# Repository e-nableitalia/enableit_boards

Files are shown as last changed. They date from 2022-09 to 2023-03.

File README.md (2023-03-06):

# enable-it
e-Nable Italia Bionic Platform

This project aims to create a general purpose hardware platform that can be used to develop bionic/electronics controlled devices

## Boards
### Controllers - controller boards with a general purpose CPU, exposing a standard bus interface (see B2BCB specifications)
* ESP32 Wroom board Rev. B - ESP32 S3 based 

### Debug - debug, testing boards
* Debug Board Rev. A, mating board useful for debug and testing purposes

## Project directory layout
- docs, contains general documents
- schematics,  contains schematics in PDF format
- build, contains CAM Output files for board production
- EAGLE, contains project EAGLE files

## Project updates
220913 - repo init, added project doc & rev. 0.9 of ESP32 controller board

220922 - added debug board, added Rev. B of control board

220927 - updated debug board to Rev. A (added bottom connectors to allow tests of stacked boards)

230305 - added EMG Module - Rev B, changed name to enable-it

## KNOWN ISSUES

- ESP32 Controller board flash programming problem, rework required to fix this issue 
- Power connectors are not correctly aligned in all the boards, rework required to fix this issue
- Wrong height of 40pin connectors (4mm instead of 3mm)
- EMG Module power issue: short circuitt between AVDD & AVSS (PS$32 AVSS connected to V+ instead of V-)

## LIMITATION OF LIABILITY.
UNDER NO CIRCUMSTANCES AND UNDER NO LEGAL THEORY, WHETHER TORT (INCLUDING NEGLIGENCE), CONTRACT, OR OTHERWISE, SHALL YOU, THE INITIAL DEVELOPER, ANY OTHER CONTRIBUTOR, OR ANY DISTRIBUTOR OF COVERED CODE, OR ANY SUPPLIER OF ANY OF SUCH PARTIES, BE LIABLE TO ANY PERSON FOR ANY INDIRECT, SPECIAL, INCIDENTAL, OR CONSEQUENTIAL DAMAGES OF ANY CHARACTER INCLUDING, WITHOUT LIMITATION, DAMAGES FOR LOSS OF GOODWILL, WORK STOPPAGE, COMPUTER FAILURE OR MALFUNCTION, OR ANY AND ALL OTHER COMMERCIAL DAMAGES OR LOSSES, EVEN IF SUCH PARTY SHALL HAVE BEEN INFORMED OF THE POSSIBILITY OF SUCH DAMAGES. THIS LIMITATION OF LIABILITY SHALL NOT APPLY TO LIABILITY FOR DEATH OR PERSONAL INJURY RESULTING FROM SUCH PARTY'S NEGLIGENCE TO THE EXTENT APPLICABLE LAW PROHIBITS SUCH LIMITATION. SOME JURISDICTIONS DO NOT ALLOW THE EXCLUSION OR LIMITATION OF INCIDENTAL OR CONSEQUENTIAL DAMAGES, SO THIS EXCLUSION AND LIMITATION MAY NOT APPLY TO YOU.

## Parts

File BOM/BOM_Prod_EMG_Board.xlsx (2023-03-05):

 |  |  | BOM
Item # | *Designator | *Qty | Manufacturer | *Mfg Part # | Description / Value | *Package/Footprint | Type | Your Instructions / Notes
1 | C10, C22, C24, C62, C63, C66 | 6 | Murata | GRM155R71H104KE14D | Multilayer Ceramic Capacitors MLCC - SMD/SMT .1UF 50V 10% 0402 | C0402 | SMD
2 | R4, R7, R55, R56 | 4 | Panasonic | ERJ-2RKF1002X | Thick Film Resistors - SMD 0402 10Kohms 1% AEC-Q200 | R0402 | SMD
3 | R1, R5, R9, R12, R15, R18, R21, R24, R27, R30, R33, R36, R39, R42, R51, R54 | 16 | Panasonic | ERJ-2GEJ106X | Thick Film Resistors - SMD 0402 10Mohms 5% Tol AEC-Q200 | R0402 | SMD
4 | C23 | 1 | Murata | GRM155R60J106ME15D | Multilayer Ceramic Capacitors MLCC - SMD/SMT 10UF 6.3V 20% 0402 | C0402 | SMD
5 | R3, R8, R11, R14, R17, R20, R23, R26, R29, R32, R35, R38, R41, R44, R53, R59 | 16 | Panasonic | ERJ-PA2F1001X | Thick Film Resistors - SMD 0402 1% 1.0Kohm Anti-Surge AEC-Q200 | R0402 | SMD
6 | R2, R6, R10, R13, R16, R19, R22, R25, R28, R31, R34, R37, R40, R43, R52, R58 | 16 | Panasonic | ERJ-PA2F1004X | Thick Film Resistors - SMD 0402 1% 1.0Mohm Anti-Surge AEC-Q200 | R0402 | SMD
7 | C64 | 1 | Murata | GRT1555C1H102JA02D | Multilayer Ceramic Capacitors MLCC - SMD/SMT 1000PF 50V 5% 0402 | C0402 | SMD
8 | C1, C5, C7, C11, C13, C15, C25, C27, C29, C31, C33, C35, C37, C39, C53, C55 | 16 | Murata | GRM155R61E105MA12D | Multilayer Ceramic Capacitors MLCC - SMD/SMT 1.0UF 25V 20% 0402 | C0402 | SMD
9 | C3, C4, C9, C17, C18, C19, C20, C21, C57, C59, C60, C61, C65 | 13 | Murata | GRM155R61E105MA12D | Multilayer Ceramic Capacitors MLCC - SMD/SMT 1.0UF 25V 20% 0402 | C0402 | SMD
10 | J9, J10 | 2 | ERNI | 224920 | Board to Board & Mezzanine Connectors 9P 0.8MM VERT FML CLASS 4 3MM SMT | 224920 | SMD
11 | C58 | 1 | Murata | GRM158R61A226ME15D | Multilayer Ceramic Capacitors MLCC - SMD/SMT 0402(1005M)/X5R/22uF/ +/-20%/10 VDC | C0402 | SMD
12 | C2, C6, C8, C12, C14, C16, C26, C28, C30, C32, C34, C36, C38, C40, C54, C56 | 16 | Murata | GRM1555C1H471FA01D | Multilayer Ceramic Capacitors MLCC - SMD/SMT 470PF 50V 1% 0402 | C0402 | SMD
13 | J1, J2 | 2 | Hirose | BM23FR0.6-8DS-0.35V(895) | Board to Board & Mezzanine Connectors 8P RCPT STRGHT SMT SIGNAL ONLY | BM23FR068DS035V895 | SMD
14 | J5 | 1 | Hirose | DF12NB-40DS-0.5V(51) | Board to Board & Mezzanine Connectors CONN RCPT 40POS SMD | DF12NB40DS05V51 | SMD
15 | J7 | 1 | Hirose | DF12NB(4.0)-40DP-0.5V(51) | Board to Board & Mezzanine Connectors CONN HDR 40POS SMD G | DF12NB4040DP05V51 | SMD
16 | S1 | 1 | TE Connectivity / Alcoswitch | GDH04S04 | DIP Switches/SIP Switches SPST 4POS REC RCKR SMT DIP SWITCH | SOIC127P813X256-8N | SMD
17 | PS1 | 1 | Maxim Integrated | MAX1697UEUT+T | MAXIM INTEGRATED PRODUCTS - MAX1697UEUT+T - CHARGE PUMP, INVERTING, SOT-23-6 | SOT95P280X145-6N | SMD
18 | U21 | 1 | Texas Instruments | TPS73225MDBVREP | LDO Voltage Regulators Mil Enh Cap-Free NMOS 250-mA LDO Reg | SOT23-5 | SMD
19 | U1 | 1 | Texas Instruments | ADS1298IPAG | Analog to Digital Converters - ADC 8Ch,24B ADC | TQFP-64 | SMD
20 | U10 | 1 | Texas Instruments | ESD401DPYR | ESD Suppressors / TVS Diodes 0.77-pF, +/-5.5V, +/-24-kV ESD protection diode in 0402 package 2-X1SON -40 to 125 | DPY0002A | SMD
21 | U12 | 1 | Texas Instruments | ESD401DPYR | ESD Suppressors / TVS Diodes 0.77-pF, +/-5.5V, +/-24-kV ESD protection diode in 0402 package 2-X1SON -40 to 125 | DPY0002A | SMD
22 | U13 | 1 | Texas Instruments | ESD401DPYR | ESD Suppressors / TVS Diodes 0.77-pF, +/-5.5V, +/-24-kV ESD protection diode in 0402 package 2-X1SON -40 to 125 | DPY0002A | SMD
23 | U14 | 1 | Texas Instruments | ESD401DPYR | ESD Suppressors / TVS Diodes 0.77-pF, +/-5.5V, +/-24-kV ESD protection diode in 0402 package 2-X1SON -40 to 125 | DPY0002A | SMD
24 | U15 | 1 | Texas Instruments | ESD401DPYR | ESD Suppressors / TVS Diodes 0.77-pF, +/-5.5V, +/-24-kV ESD protection diode in 0402 package 2-X1SON -40 to 125 | DPY0002A | SMD
25 | U17 | 1 | Texas Instruments | ESD401DPYR | ESD Suppressors / TVS Diodes 0.77-pF, +/-5.5V, +/-24-kV ESD protection diode in 0402 package 2-X1SON -40 to 125 | DPY0002A | SMD
26 | U11, U18 | 2 | Texas Instruments | ESD401DPYR | ESD Suppressors / TVS Diodes 0.77-pF, +/-5.5V, +/-24-kV ESD protection diode in 0402 package 2-X1SON -40 to 125 | DPY0002A | SMD
27 | U2 | 1 | Texas Instruments | ESD401DPYR | ESD Suppressors / TVS Diodes 0.77-pF, +/-5.5V, +/-24-kV ESD protection diode in 0402 package 2-X1SON -40 to 125 | DPY0002A | SMD
28 | U3 | 1 | Texas Instruments | ESD401DPYR | ESD Suppressors / TVS Diodes 0.77-pF, +/-5.5V, +/-24-kV ESD protection diode in 0402 package 2-X1SON -40 to 125 | DPY0002A | SMD
29 | U4 | 1 | Texas Instruments | ESD401DPYR | ESD Suppressors / TVS Diodes 0.77-pF, +/-5.5V, +/-24-kV ESD protection diode in 0402 package 2-X1SON -40 to 125 | DPY0002A | SMD
30 | U5 | 1 | Texas Instruments | ESD401DPYR | ESD Suppressors / TVS Diodes 0.77-pF, +/-5.5V, +/-24-kV ESD protection diode in 0402 package 2-X1SON -40 to 125 | DPY0002A | SMD
31 | U6 | 1 | Texas Instruments | ESD401DPYR | ESD Suppressors / TVS Diodes 0.77-pF, +/-5.5V, +/-24-kV ESD protection diode in 0402 package 2-X1SON -40 to 125 | DPY0002A | SMD
32 | U7 | 1 | Texas Instruments | ESD401DPYR | ESD Suppressors / TVS Diodes 0.77-pF, +/-5.5V, +/-24-kV ESD protection diode in 0402 package 2-X1SON -40 to 125 | DPY0002A | SMD
33 | U8 | 1 | Texas Instruments | ESD401DPYR | ESD Suppressors / TVS Diodes 0.77-pF, +/-5.5V, +/-24-kV ESD protection diode in 0402 package 2-X1SON -40 to 125 | DPY0002A | SMD
34 | U9 | 1 | Texas Instruments | ESD401DPYR | ESD Suppressors / TVS Diodes 0.77-pF, +/-5.5V, +/-24-kV ESD protection diode in 0402 package 2-X1SON -40 to 125 | DPY0002A | SMD
Need a quick and accurante quote? Need an efficient production? Please read SMT Ordering Necessary Files & Info in 1 minute. Thank you very much! (https://www.pcbway.com/smt_ordering_guide.html)
Click for Instructions on How to Create a BOM (https://www.pcbway.com/blog/PCB_Assembly/How_to_Build_a_BOM__Bill_Of_Materials_.html)

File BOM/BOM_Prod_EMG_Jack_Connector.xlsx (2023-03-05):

 |  |  | BOM
Item # | *Designator | *Qty | Manufacturer | *Mfg Part # | Description / Value | *Package/Footprint | Type | Your Instructions / Notes
1 | J1, J6 | 2 | Hirose | BM23FR0.6-8DP-0.35V(51) | Board to Board & Mezzanine Connectors 8P HDR STRGHT SMT SIGNAL ONLY | BM23FR068DP035V51 | SMD
2 | J2, J3, J4, J7, J8, J9, J10, J17 | 6 | CUI | SJ1-3533N | 3.5 mm Right-Angle Stereo Jack, 3 Pin PCB Mount, Threaded w/ Nut Check | CUI_SJ1-3533 | thru-hole
Need a quick and accurante quote? Need an efficient production? Please read SMT Ordering Necessary Files & Info in 1 minute. Thank you very much! (https://www.pcbway.com/smt_ordering_guide.html)
Click for Instructions on How to Create a BOM (https://www.pcbway.com/blog/PCB_Assembly/How_to_Build_a_BOM__Bill_Of_Materials_.html)

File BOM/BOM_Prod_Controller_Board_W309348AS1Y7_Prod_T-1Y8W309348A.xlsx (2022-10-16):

 |  |  | W309348AS1Y7 T-1Y8W309348A 05PCS BOM (Bill of Materials)
Item # | *Designator | *Qty | Manufacturer | *Mfg Part # | Description / Value | *Package/Footprint | Type | Your Instructions / Notes
1 | J2 | 1 |  |  | SMD solder JUMPER , | SJ | DNS
2 | J8 | 1 | Hirose | ZX62-AB-5PA | USB Connectors MICRO AB RECEPT RA SMT BTTM MNT | ZX62-AB-5PA | SMD
3 | C3 | 1 | Murata | GRM155R71H104KE14D | Multilayer Ceramic Capacitors MLCC - SMD/SMT .1UF 50V 10% 0402 | C0402 | SMD
4 | R9, R10 | 2 | Panasonic | ERJ-2GE0R00X | Thick Film Resistors - SMD 0402 Zero ohms 5% Tol AEC-Q200 | R0402 | SMD
5 | R3 | 1 | Panasonic | ERJ-2RKF1003X | Thick Film Resistors - SMD 0402 100Kohms 1% AEC-Q200 | R0402 | SMD
6 | R1 | 1 | Panasonic | ERJ-2RKF1002X | Thick Film Resistors - SMD 0402 10Kohms 1% AEC-Q200 | R0402 | SMD
7 | C6 | 1 | Murata | GRM155R60J106ME15D | Multilayer Ceramic Capacitors MLCC - SMD/SMT 10UF 6.3V 20% 0402 | C0402 | SMD
8 | R6 | 1 | Panasonic | ERJ-PA2F1004X | Thick Film Resistors - SMD 0402 1% 1.0Mohm Anti-Surge AEC-Q200 | R0402 | SMD
9 | R11 | 1 | Panasonic | ERJ-PA2F1001X | Thick Film Resistors - SMD 0402 1% 1.0Kohm Anti-Surge AEC-Q200 | R0402 | SMD
10 | C5 | 1 | Murata | GRM155R61E105MA12D | Multilayer Ceramic Capacitors MLCC - SMD/SMT 1.0UF 25V 20% 0402 | C0402 | SMD
11 | R2 | 1 | Panasonic | ERJ-2RKF2212X | Thick Film Resistors - SMD 0402 22.1Kohms 1% AEC-Q200 | R0402 | SMD
12 | J3 | 1 | ERNI | 224920 | Board to Board & Mezzanine Connectors 9P 0.8MM VERT FML CLASS 4 3MM SMT | 224920 | SMD
13 | C2 | 1 | Murata | GRM158R61A226ME15D | Multilayer Ceramic Capacitors MLCC - SMD/SMT 0402(1005M)/X5R/22uF/ +/-20%/10 VDC | C0402 | SMD
14 | C1, C4 | 2 | Samsung | CL10A226MO7JZNC | Multilayer Ceramic Capacitors MLCC - SMD/SMT 22uF+/-20% 16V X5R 1 0603 | C0603 | SMD
15 | R7 | 1 | Panasonic | ERJ-2RHD243X | Thick Film Resistors - SMD 0402 24Kohms 0.5%AEC-Q200 | R0402 | SMD
16 | R5 | 1 | Panasonic | ERJ-2RKF3902X | Thick Film Resistors - SMD 0402 39Kohms 1% AEC-Q200 | R0402 | SMD
17 | C11 | 1 | Kemet | C0805C472KDRACTU | Multilayer Ceramic Capacitors MLCC - SMD/SMT 1kV 4700pF X7R 0805 10% | 0805-R2013X50N | SMD
18 | PWR | 1 | MOLEX | 530470310 | Headers & Wire Housings VERTICAL HDR 3P | 53047-03 | SMD
19 | I2C | 1 | MOLEX | 532610271 | Headers & Wire Housings 1.25MM HDR 2 CKT Right-Angle | 53261-02 | SMD
20 | R4, R8 | 2 | Panasonic | ERJ-2RKF7502X | Thick Film Resistors - SMD 0402 75Kohms 1% AEC-Q200 | R0402 | SMD
21 | IC3 | 1 | Silicon Labs | CP2102N-A02-GQFN20R | USB Interface IC USBXpress - USB to UART Bridge QFN20 | CP2102NA02GQFN20 | SMD
22 | J1 | 1 | Hirose | DF12NB(4.0)-40DP-0.5V(51) | Board to Board & Mezzanine Connectors CONN HDR 40POS SMD G | DF12NB4040DP05V51 | SMD
23 | IC1 | 1 | Espressif Systems | ESP32-S3-WROOM-1-N8R2 | Multiprotocol Modules SMD Module, ESP32-S3R2, 2 MB PSRAM, 8 MB SPI Flash, PCB Antenna | ESP32S3WROOM1N8R2 | SMD
24 | S1 | 1 | C & K COMPONENTS | KMT211NGLFS | Tactile Switches SPST N.O. GULLWING FOR SMT | KMT211NGLFS | SMD
25 | IC2 | 1 | Monolithic Power Systems (MPS) | MPM3610GQV-P | Switching Voltage Regulators 24V/1A DC/DC Mini- Module Reg w Inductr | MPM3610GQVP | SMD
26 | D2 | 1 | Nexperia | PMEG6020AELPX | Schottky Diodes & Rectifiers PMEG6020AELP/SOD128/FlatPower | SODFL4725X110N | SMD
27 | D1 | 1 | Nexperia | PRTR5V0U2X,215 | ESD Suppressors / TVS Diodes PRTR5V0U2X/SOT143/SOT4 | SOT190P230X110-4N | SMD
Need a quick and accurante quote? Need an efficient production? Please read SMT Ordering Necessary Files & Info in 1 minute. Thank you very much! (https://www.pcbway.com/smt_ordering_guide.html)
Click for Instructions on How to Create a BOM (https://www.pcbway.com/blog/PCB_Assembly/How_to_Build_a_BOM__Bill_Of_Materials_.html)

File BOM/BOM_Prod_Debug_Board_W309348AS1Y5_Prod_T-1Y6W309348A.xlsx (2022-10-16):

 |  |  | W309348AS1Y7 T-1Y8W309348A 05PCS BOM (Bill of Materials)
Item # | *Designator | *Qty | Manufacturer | *Mfg Part # | Description / Value | *Package/Footprint | Type | Your Instructions / Notes
1 | J3, J6 | 2 | ERNI | 224920 | Board to Board & Mezzanine Connectors 9P 0.8MM VERT FML CLASS 4 3MM SMT | 224920 | SMD
2 | J5 | 1 | Hirose | DF12NB-40DS-0.5V(51) | Board to Board & Mezzanine Connectors CONN RCPT 40POS SMD | DF12NB40DS05V51 | SMD
3 | J7 | 1 | Hirose | DF12NB(4.0)-40DP-0.5V(51) | Board to Board & Mezzanine Connectors CONN HDR 40POS SMD G | DF12NB4040DP05V51 | SMD
4 | J4 | 1 | Harwin | M50-3031042 | Headers & Wire Housings 10 WAY SIL VERT PC TAIL SKT | M503031042 | DNS | Do not populate
5 | J1, J2 | 2 | Harwin | M50-3032042 | Headers & Wire Housings 20 WAY SIL VERT PC TAIL SKT | M503032042 | DNS | Do not populate
6
7
8
9
10
11
12
13
14
15
16
17
18
19
20
21
22
23
24
25
26
27
Need a quick and accurante quote? Need an efficient production? Please read SMT Ordering Necessary Files & Info in 1 minute. Thank you very much! (https://www.pcbway.com/smt_ordering_guide.html)
Click for Instructions on How to Create a BOM (https://www.pcbway.com/blog/PCB_Assembly/How_to_Build_a_BOM__Bill_Of_Materials_.html)

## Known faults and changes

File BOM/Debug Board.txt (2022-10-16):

Partlist exported from H:/Drive condivisi/e-Nable Italia/R&D Projects/EAGLE/e-Bionic/Debug Board.sch at 28/09/2022 07:59

Qty Value                     Device                    Package           Parts  Description                                                             DESCRIPTION                                                             HEIGHT MANUFACTURER_NAME MANUFACTURER_PART_NUMBER  MOUSER_PART_NUMBER   MOUSER_PRICE-STOCK                                                                                           
2   224920                    224920                    224920            J3, J6 Board to Board & Mezzanine Connectors 9P 0.8MM VERT FML CLASS 4 3MM SMT Board to Board & Mezzanine Connectors 9P 0.8MM VERT FML CLASS 4 3MM SMT 3.96mm ERNI              224920                    305-224920           https://www.mouser.co.uk/ProductDetail/ERNI/224920?qs=Kh9WxvXxjWmfiTh6L%2FvUxg%3D%3D                         
1   DF12NB-40DS-0.5V_51_      DF12NB-40DS-0.5V_51_      DF12NB40DS05V51   J5     Board to Board & Mezzanine Connectors CONN RCPT 36POS SMD               Board to Board & Mezzanine Connectors CONN RCPT 36POS SMD               2.9mm  Hirose            DF12NB-40DS-0.5V(51)      798-DF12NB40DS0551   https://www.mouser.co.uk/ProductDetail/Hirose-Connector/DF12NB-40DS-0.5V51?qs=DPoM0jnrROV9WbEBnogTmg%3D%3D   
1   DF12NB_4.0_-40DP-0.5V_51_ DF12NB_4.0_-40DP-0.5V_51_ DF12NB4040DP05V51 J7     Board to!! Board !! & Mezzanine Connectors CONN HDR 40POS SMD G         Board to!! Board !! & Mezzanine Connectors CONN HDR 40POS SMD G         3.5mm  Hirose            DF12NB(4.0)-40DP-0.5V(51) 798-DF12NB4040DP0551 https://www.mouser.co.uk/ProductDetail/Hirose-Connector/DF12NB4.0-40DP-0.5V51?qs=DPoM0jnrROUKZpllIjGjYw%3D%3D
1   M50-3031042               M50-3031042               M503031042        J4     Headers & Wire Housings 10 WAY SIL VERT PC TAIL SKT                     Headers & Wire Housings 10 WAY SIL VERT PC TAIL SKT                     4.55mm Harwin            M50-3031042               855-M50-3031042      https://www.mouser.co.uk/ProductDetail/Harwin/M50-3031042?qs=%252BdQmOuGyFcGr7bDrWORUuA%3D%3D                
2   M50-3032042               M50-3032042               M503032042        J1, J2 Headers & Wire Housings 20 WAY SIL VERT PC TAIL SKT                     Headers & Wire Housings 20 WAY SIL VERT PC TAIL SKT                     4.55mm Harwin            M50-3032042               855-M50-3032042      https://www.mouser.co.uk/ProductDetail/Harwin/M50-3032042?qs=%252BdQmOuGyFcG1Q4VMzC2p1Q%3D%3D

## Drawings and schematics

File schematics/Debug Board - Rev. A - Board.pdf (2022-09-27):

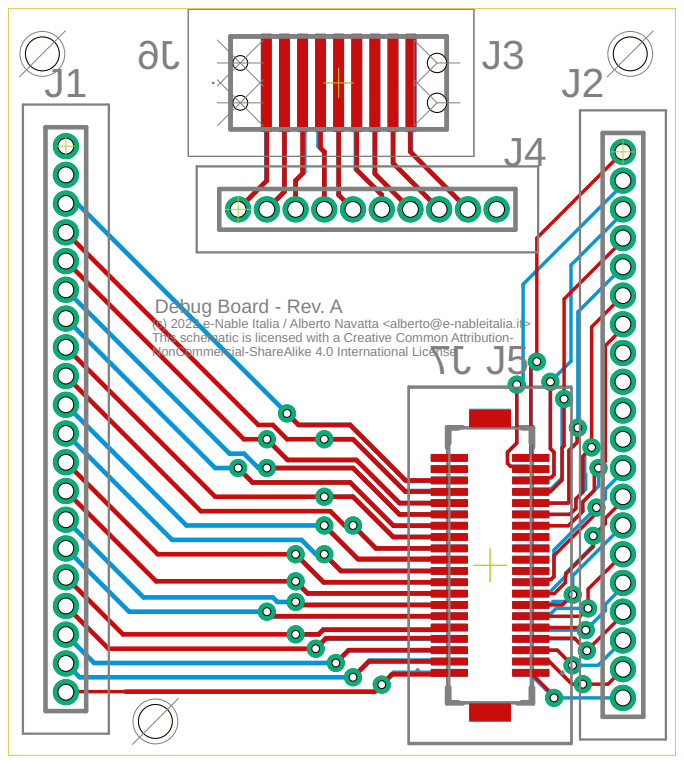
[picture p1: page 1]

Debug Board - Rev. A
(c) 2022 e-Nable Italia / Alberto Navatta <alberto@e-nableitalia.it>
This schematic is licensed with a Creative Common Attribution- NonCommercial-ShareAlike 4.0 International License

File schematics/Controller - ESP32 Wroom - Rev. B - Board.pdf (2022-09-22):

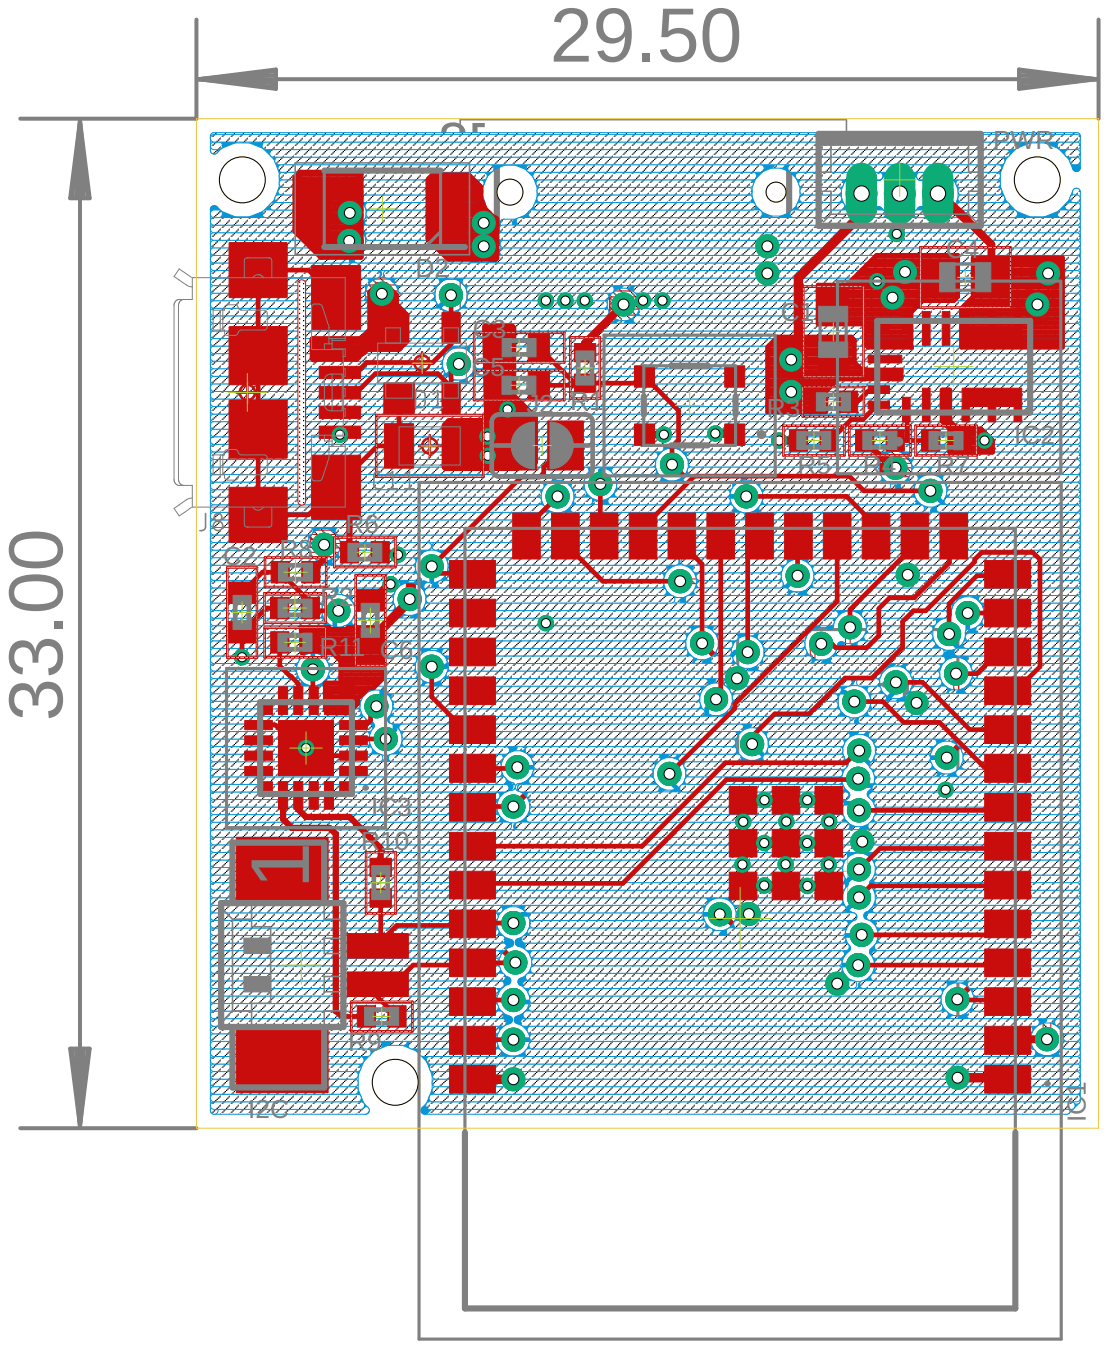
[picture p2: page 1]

(c) 2022 e-Nable Italia / Alberto Navatta <alberto@e-nableitalia.it> This schematic is licensed with a Creative Common Attribution- NonCommercial-ShareAlike 4.0 International License Controller Board - ESP32 Wroom - Rev. A1J 3J 1 33.00 29.50 C5 IC1 J2 R1 C3 D2 IC2 R3 C4 R5 R4 R7 R6 C1 I2C IC3 R2 C R8 2 R9R10 R11 C6 PWR

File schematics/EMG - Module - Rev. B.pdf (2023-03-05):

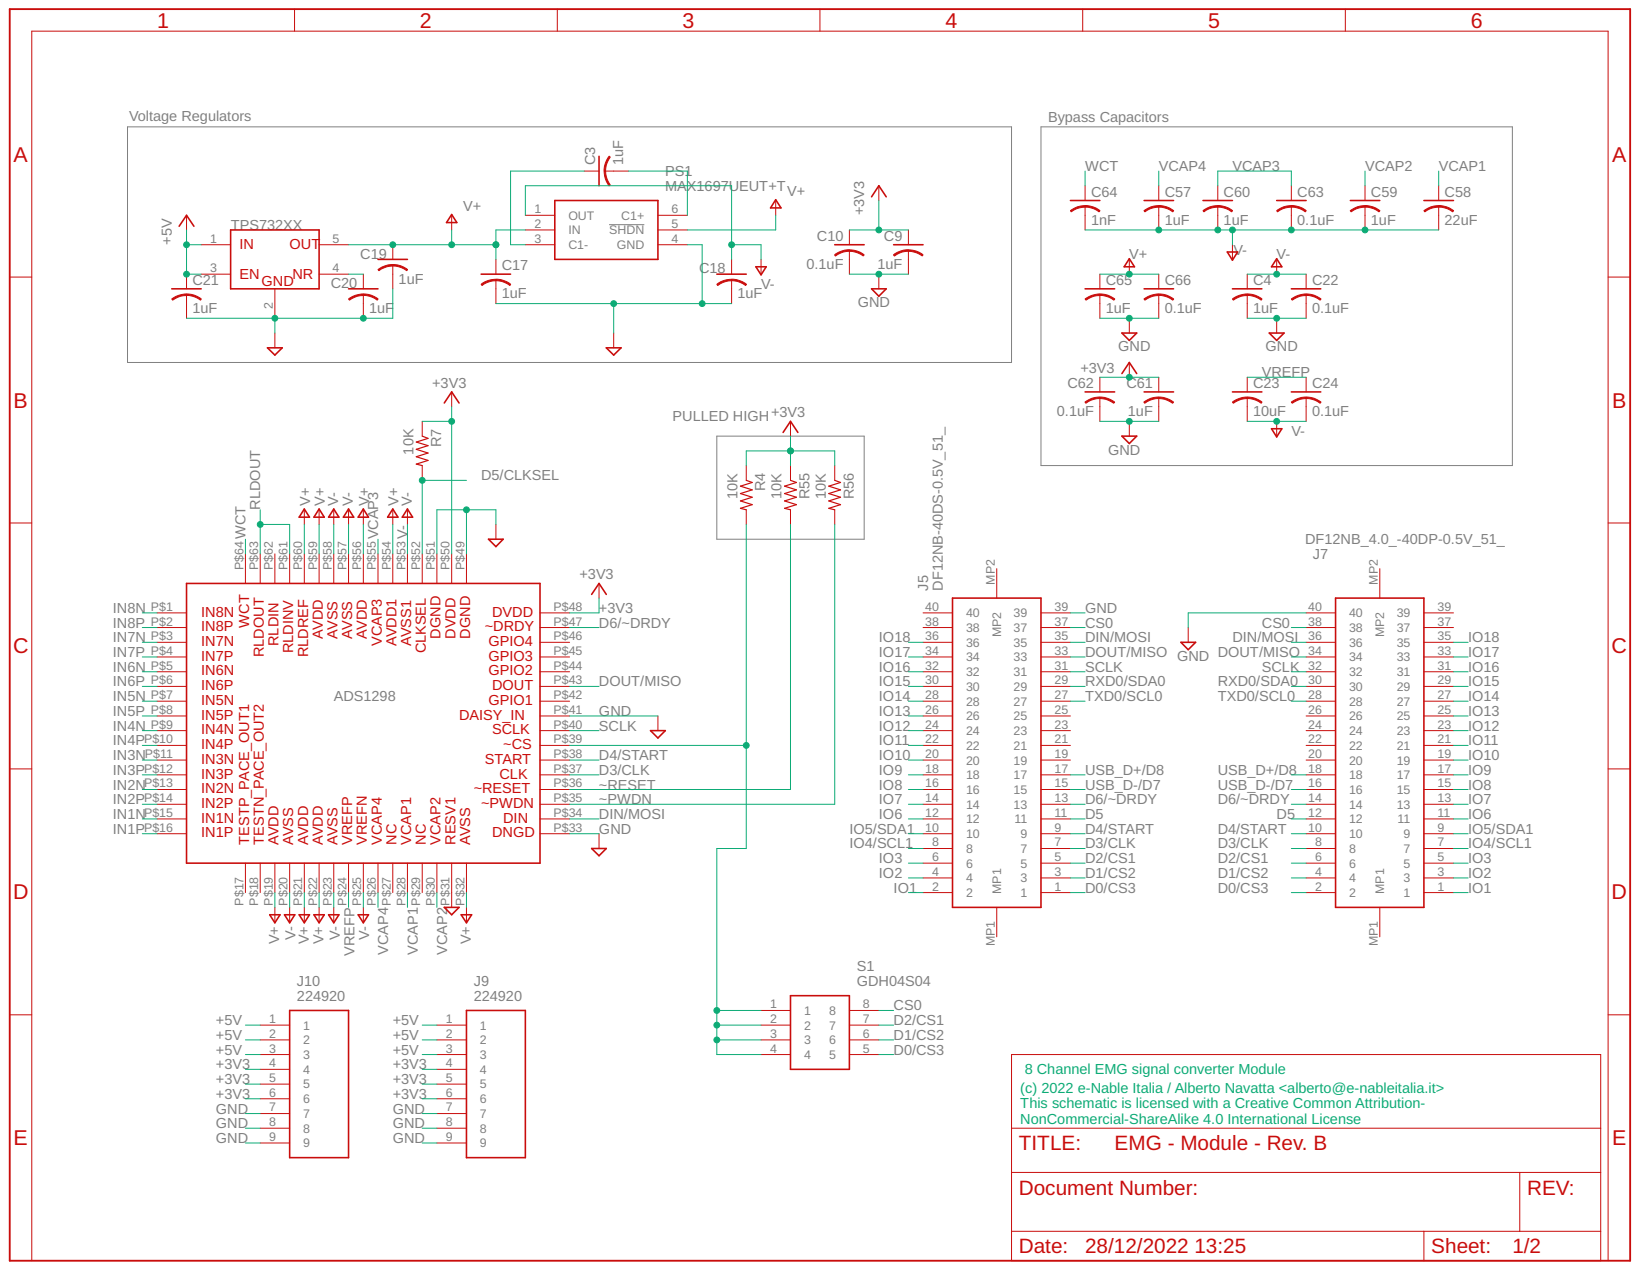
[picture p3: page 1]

8 Channel EMG signal converter Module
(c) 2022 e-Nable Italia / Alberto Navatta <alberto@e-nableitalia.it> This schematic is licensed with a Creative Common Attribution- NonCommercial-ShareAlike 4.0 International License

Document Number: | REV:

Date: 28/12/2022 13:25 | Sheet: 1/2

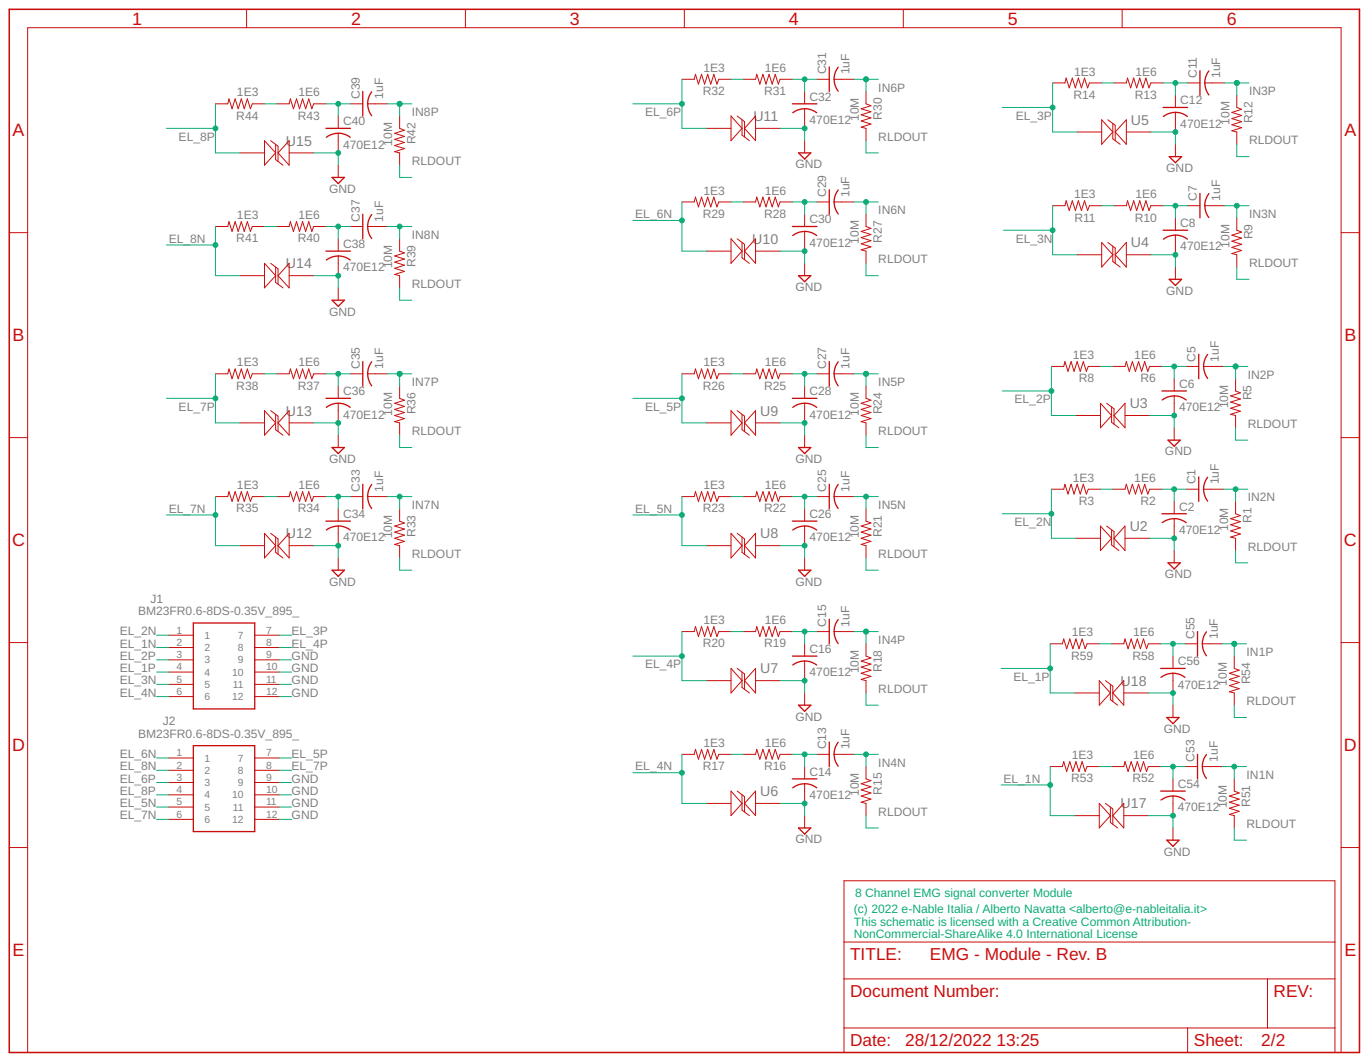
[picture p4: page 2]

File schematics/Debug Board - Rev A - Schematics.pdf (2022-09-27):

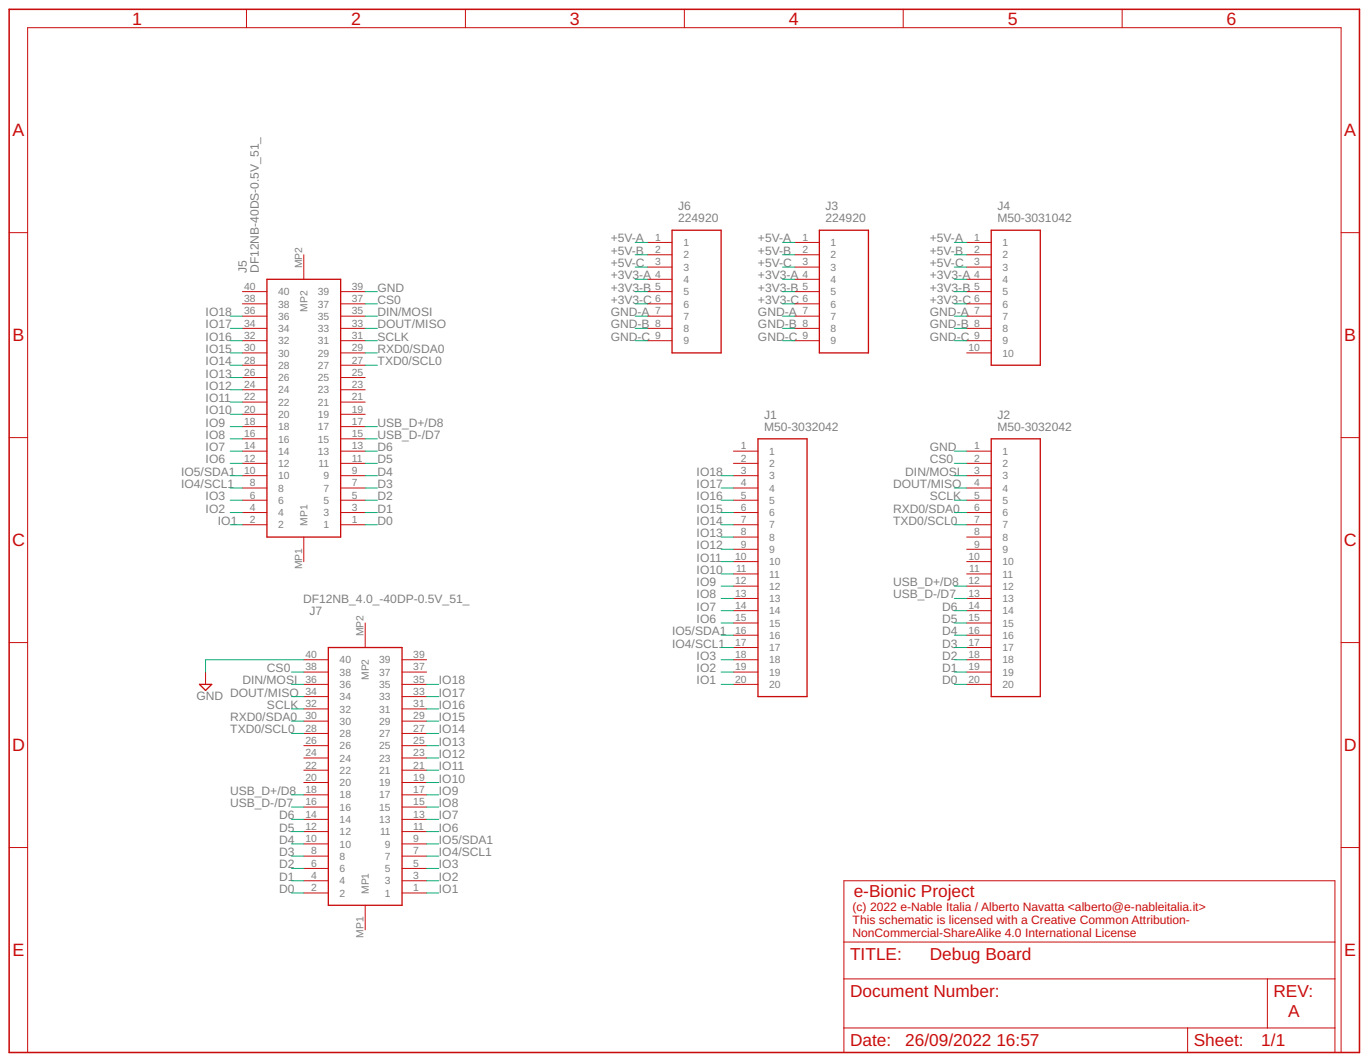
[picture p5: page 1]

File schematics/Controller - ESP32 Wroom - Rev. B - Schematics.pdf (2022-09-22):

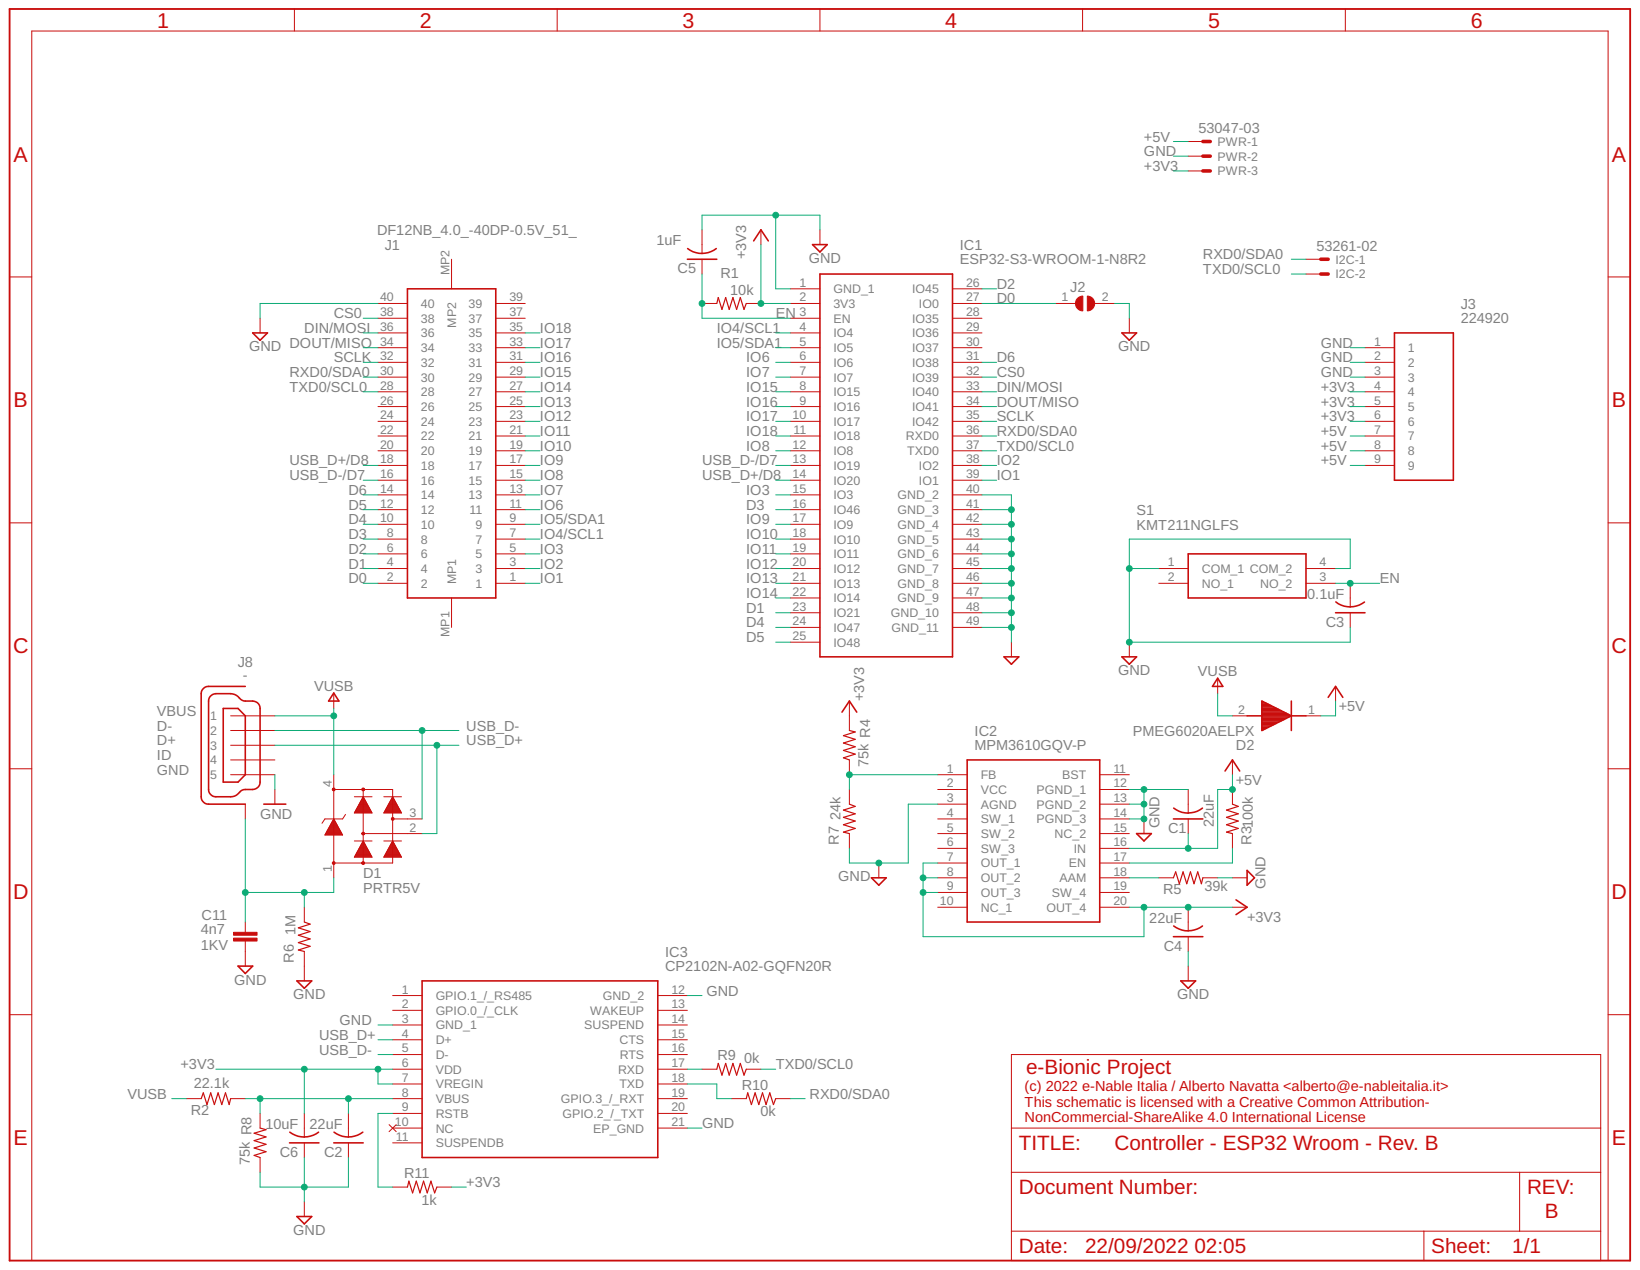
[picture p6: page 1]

Document Number: | REV:

Date: 22/09/2022 02:05 | Sheet: 1/1

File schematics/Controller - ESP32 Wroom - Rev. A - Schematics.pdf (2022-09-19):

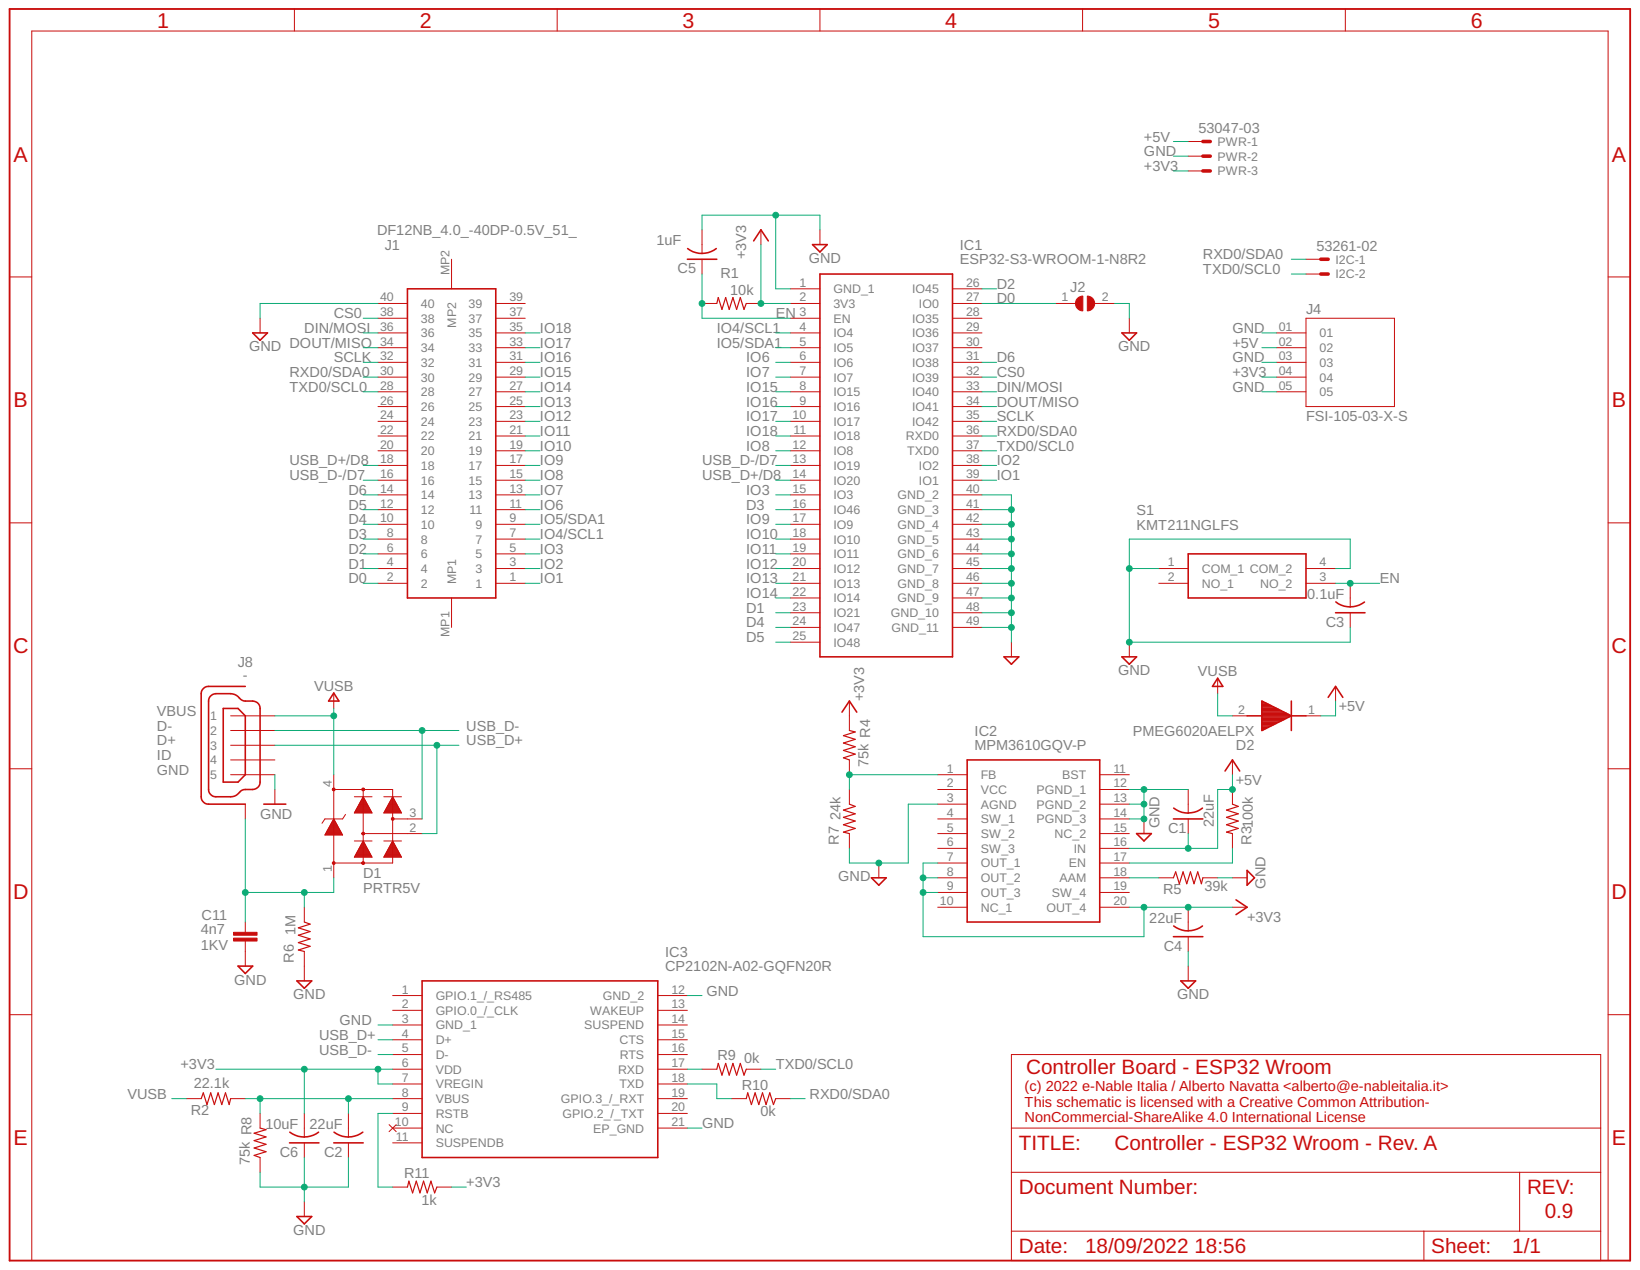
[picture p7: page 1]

Document Number: | REV:

Date: 18/09/2022 18:56 | Sheet: 1/1

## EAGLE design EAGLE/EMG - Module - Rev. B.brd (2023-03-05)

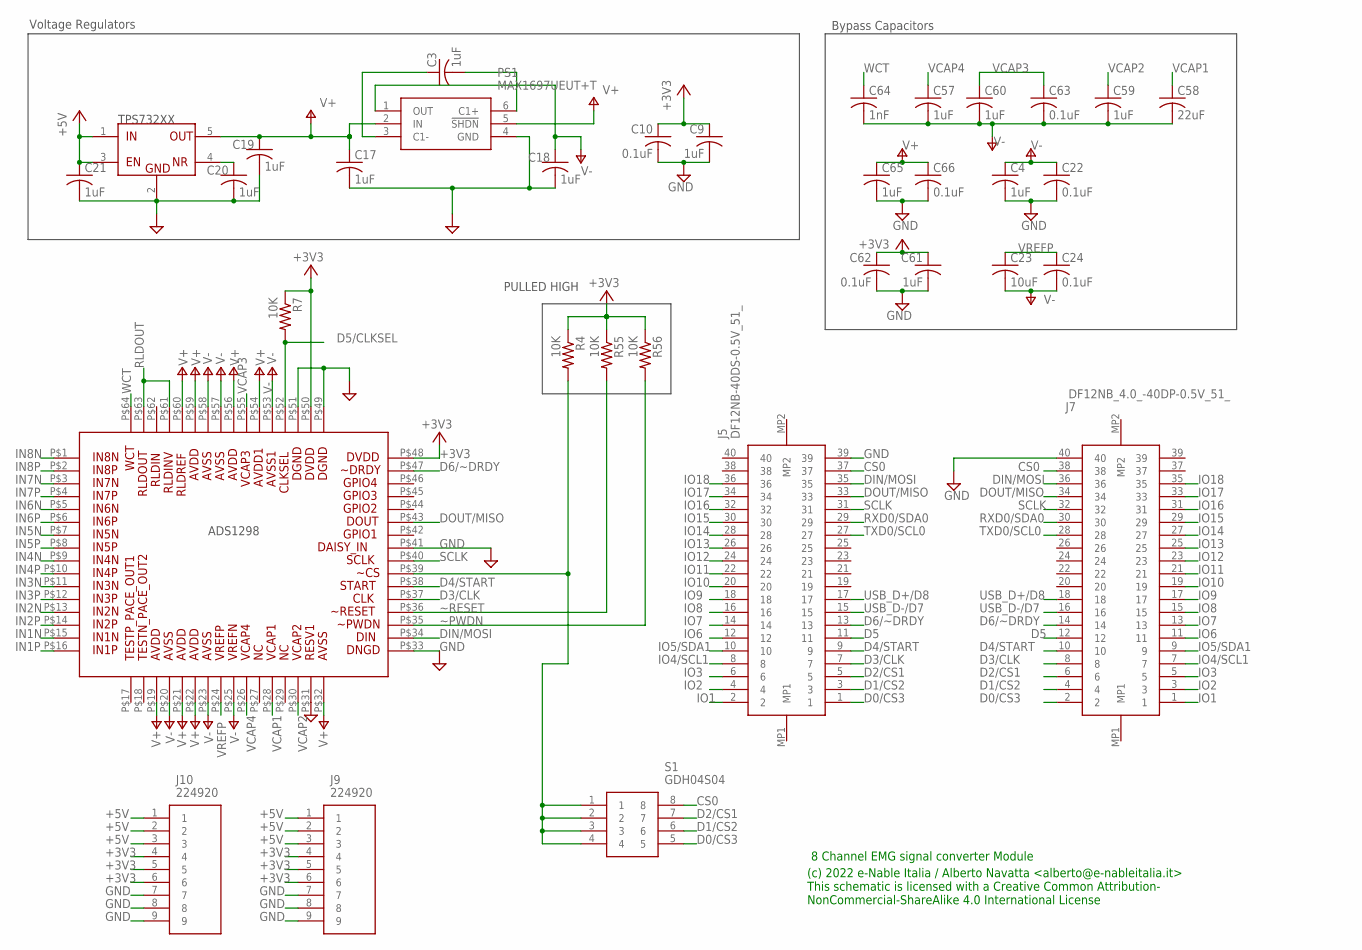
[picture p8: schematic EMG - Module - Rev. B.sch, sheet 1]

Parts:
C3, C4, C9, C17, C18, C19, C20, C21, C57, C59, C60, C61, C65: 1uF; C0402
C10, C22, C24, C62, C63, C66: 0.1uF; C0402
C23: 10uF; C0402
C58: 22uF; C0402
C64: 1nF; C0402
J5: DF12NB-40DS-0.5V_51_; DF12NB40DS05V51
J7: DF12NB_4.0_-40DP-0.5V_51_; DF12NB4040DP05V51
J9, J10: 224920
PS1: MAX1697UEUT+T; SOT95P280X145-6N
R4, R7, R55, R56: 10K; R0402
S1: GDH04S04; SOIC127P813X256-8N
U1: U1; TQFP-64
U21: TPS732XX; SOT23-5

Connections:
+3V3: C9.1, C10.1, C61.1, C62.1, J9.4, J9.5, J9.6, J10.4, J10.5, J10.6, R4.1, R7.1, R55.1, R56.1, U1.P$48, U1.P$50
+5V: C21.1, J9.1, J9.2, J9.3, J10.1, J10.2, J10.3, U21.1 (IN), U21.3 (EN)
CS0: J5.37, J7.38, S1.8
D0/CS3: J5.1, J7.2, S1.5
D1/CS2: J5.3, J7.4, S1.6
D2/CS1: J5.5, J7.6, S1.7
D3/CLK: J5.7, J7.8, U1.P$37
D4/START: J5.9, J7.10, U1.P$38
D5: J5.11, J7.12
D5/CLKSEL: R7.2, U1.P$52
D6/~DRDY: J5.13, J7.14, U1.P$47
DIN/MOSI: J5.35, J7.36, U1.P$34
DOUT/MISO: J5.33, J7.34, U1.P$43
GND: C4.2, C9.2, C10.2, C17.2, C18.2, C19.2, C20.2, C21.2, C22.2, C61.2, C62.2, C65.2, C66.2, J5.39, J7.40, J9.7, J9.8, J9.9, J10.7, J10.8, J10.9, PS1.4 (GND), U1.P$31, U1.P$33, U1.P$41, U1.P$49, U1.P$51, U21.2 (GND); also elsewhere on the board
IN1N: U1.P$15; also elsewhere on the board
IN1P: U1.P$16; also elsewhere on the board
IN2N: U1.P$13; also elsewhere on the board
IN2P: U1.P$14; also elsewhere on the board
IN3N: U1.P$11; also elsewhere on the board
IN3P: U1.P$12; also elsewhere on the board
IN4N: U1.P$9; also elsewhere on the board
IN4P: U1.P$10; also elsewhere on the board
IN5N: U1.P$7; also elsewhere on the board
IN5P: U1.P$8; also elsewhere on the board
IN6N: U1.P$5; also elsewhere on the board
IN6P: U1.P$6; also elsewhere on the board
IN7N: U1.P$3; also elsewhere on the board
IN7P: U1.P$4; also elsewhere on the board
IN8N: U1.P$1; also elsewhere on the board
IN8P: U1.P$2; also elsewhere on the board
IO1: J5.2, J7.1
IO2: J5.4, J7.3
IO3: J5.6, J7.5
IO4/SCL1: J5.8, J7.7
IO5/SDA1: J5.10, J7.9
IO6: J5.12, J7.11
IO7: J5.14, J7.13
IO8: J5.16, J7.15
IO9: J5.18, J7.17
IO10: J5.20, J7.19
IO11: J5.22, J7.21
IO12: J5.24, J7.23
IO13: J5.26, J7.25
IO14: J5.28, J7.27
IO15: J5.30, J7.29
IO16: J5.32, J7.31
IO17: J5.34, J7.33
IO18: J5.36, J7.35
unnamed: C3.1, PS1.3 (C1-)
unnamed: C3.2, PS1.6 (C1+)
unnamed: C20.1, U21.4 (NR)
RLDOUT: U1.P$61, U1.P$63; also elsewhere on the board
RXD0/SDA0: J5.29, J7.30
SCLK: J5.31, J7.32, U1.P$40
TXD0/SCL0: J5.27, J7.28
USB_D+/D8: J5.17, J7.18
USB_D-/D7: J5.15, J7.16
V+: C17.1, C19.1, C65.1, C66.1, PS1.2 (IN), PS1.5 (!SHDN), U1.P$19, U1.P$21, U1.P$22, U1.P$32, U1.P$54, U1.P$56, U1.P$59, U1.P$60, U21.5 (OUT)
V-: C4.1, C18.1, C22.1, C23.2, C24.2, C57.2, C58.2, C59.2, C60.2, C63.2, C64.2, PS1.1 (OUT), U1.P$20, U1.P$23, U1.P$25, U1.P$53, U1.P$57, U1.P$58
VCAP1: C58.1, U1.P$28
VCAP2: C59.1, U1.P$30
VCAP3: C60.1, C63.1, U1.P$55
VCAP4: C57.1, U1.P$26
VREFP: C23.1, C24.1, U1.P$24
WCT: C64.1, U1.P$64
~CS: R4.2, S1.1, S1.2, S1.3, S1.4, U1.P$39
~PWDN: R56.2, U1.P$35
~RESET: R55.2, U1.P$36

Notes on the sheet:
PULLED HIGH
Voltage Regulators
Bypass Capacitors
(c) 2022 e-Nable Italia / Alberto Navatta <alberto@e-nableitalia.it> This schematic is licensed with a Creative Common Attribution- NonCommercial-ShareAlike 4.0 International License
8 Channel EMG signal converter Module

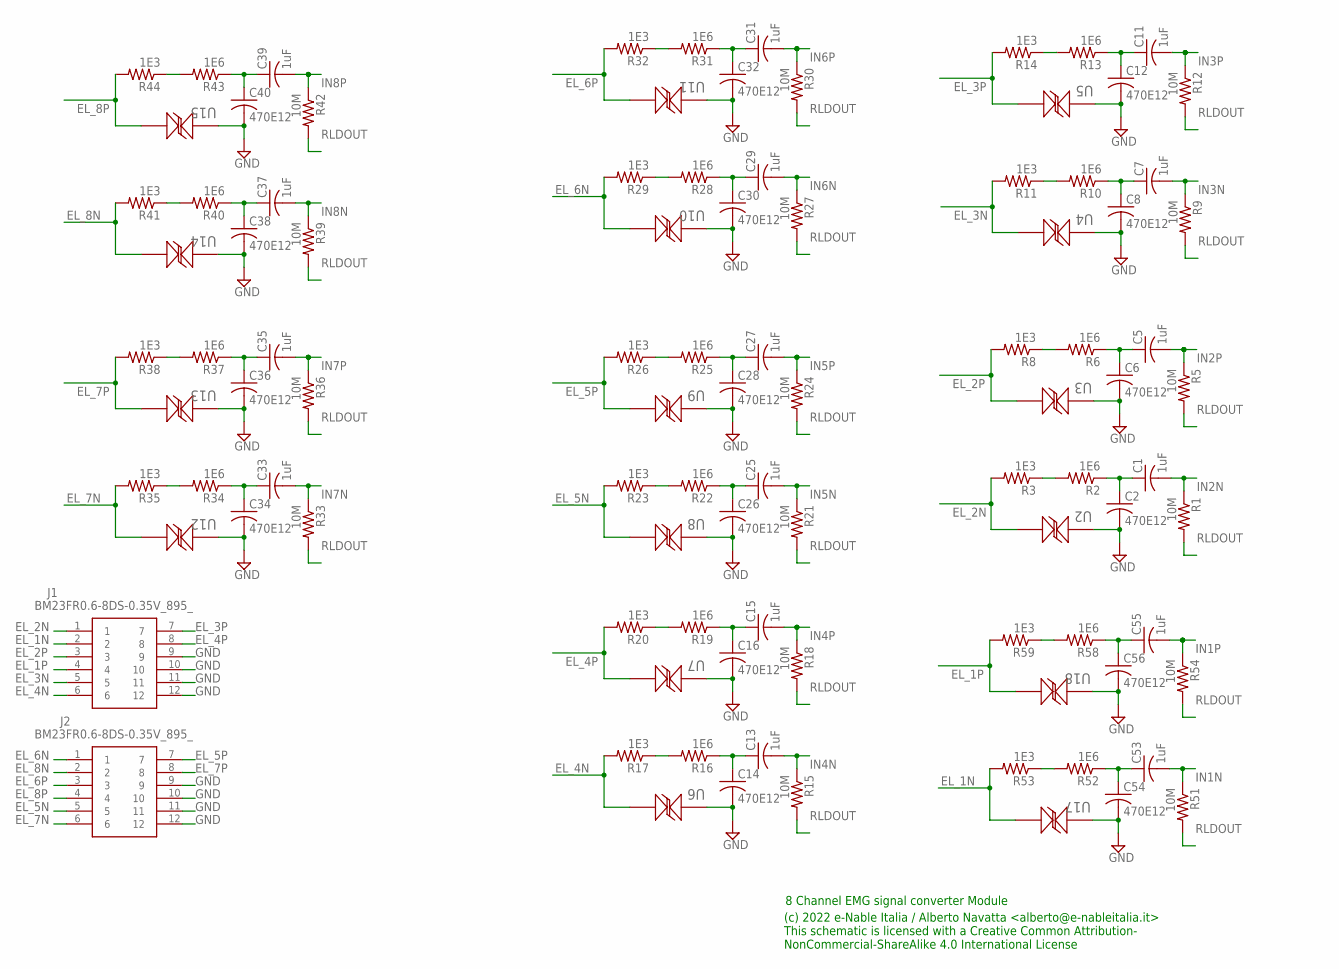
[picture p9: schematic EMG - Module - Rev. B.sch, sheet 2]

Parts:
C1, C5, C7, C11, C13, C15, C25, C27, C29, C31, C33, C35, C37, C39, C53, C55: 1uF; C0402
C2, C6, C8, C12, C14, C16, C26, C28, C30, C32, C34, C36, C38, C40, C54, C56: 470E12; C0402
J1, J2: BM23FR0.6-8DS-0.35V_895_; BM23FR068DS035V895
R1, R5, R9, R12, R15, R18, R21, R24, R27, R30, R33, R36, R39, R42, R51, R54: 10M; R0402
R2, R6, R10, R13, R16, R19, R22, R25, R28, R31, R34, R37, R40, R43, R52, R58: 1E6; R0402
R3, R8, R11, R14, R17, R20, R23, R26, R29, R32, R35, R38, R41, R44, R53, R59: 1E3; R0402
U2: U2; DPY0002A
U3: U3; DPY0002A
U4: U4; DPY0002A
U5: U5; DPY0002A
U6: U6; DPY0002A
U7: U7; DPY0002A
U8: U8; DPY0002A
U9: U9; DPY0002A
U10: U10; DPY0002A
U11, U18: U18; DPY0002A
U12: U12; DPY0002A
U13: U13; DPY0002A
U14: U14; DPY0002A
U15: U15; DPY0002A
U17: U17; DPY0002A

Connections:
EL_1N: J1.2, R53.2, U17.2
EL_1P: J1.4, R59.2, U18.2
EL_2N: J1.1, R3.2, U2.2
EL_2P: J1.3, R8.2, U3.2
EL_3N: J1.5, R11.2, U4.2
EL_3P: J1.7, R14.2, U5.2
EL_4N: J1.6, R17.2, U6.2
EL_4P: J1.8, R20.2, U7.2
EL_5N: J2.5, R23.2, U8.2
EL_5P: J2.7, R26.2, U9.2
EL_6N: J2.1, R29.2, U10.2
EL_6P: J2.3, R32.2, U11.2
EL_7N: J2.6, R35.2, U12.2
EL_7P: J2.8, R38.2, U13.2
EL_8N: J2.2, R41.2, U14.2
EL_8P: J2.4, R44.2, U15.2
GND: C2.2, C6.2, C8.2, C12.2, C14.2, C16.2, C26.2, C28.2, C30.2, C32.2, C34.2, C36.2, C38.2, C40.2, C54.2, C56.2, J1.9, J1.10, J1.11, J1.12, J2.9, J2.10, J2.11, J2.12, U2.1, U3.1, U4.1, U5.1, U6.1, U7.1, U8.1, U9.1, U10.1, U11.1, U12.1, U13.1, U14.1, U15.1, U17.1, U18.1; also elsewhere on the board
IN1N: C53.2, R51.1; also elsewhere on the board
IN1P: C55.2, R54.1; also elsewhere on the board
IN2N: C1.2, R1.1; also elsewhere on the board
IN2P: C5.2, R5.1; also elsewhere on the board
IN3N: C7.2, R9.1; also elsewhere on the board
IN3P: C11.2, R12.1; also elsewhere on the board
IN4N: C13.2, R15.1; also elsewhere on the board
IN4P: C15.2, R18.1; also elsewhere on the board
IN5N: C25.2, R21.1; also elsewhere on the board
IN5P: C27.2, R24.1; also elsewhere on the board
IN6N: C29.2, R27.1; also elsewhere on the board
IN6P: C31.2, R30.1; also elsewhere on the board
IN7N: C33.2, R33.1; also elsewhere on the board
IN7P: C35.2, R36.1; also elsewhere on the board
IN8N: C37.2, R39.1; also elsewhere on the board
IN8P: C39.2, R42.1; also elsewhere on the board
unnamed: C1.1, C2.1, R2.1
unnamed: R2.2, R3.1
unnamed: C5.1, C6.1, R6.1
unnamed: R6.2, R8.1
unnamed: C7.1, C8.1, R10.1
unnamed: R10.2, R11.1
unnamed: C11.1, C12.1, R13.1
unnamed: R13.2, R14.1
unnamed: C13.1, C14.1, R16.1
unnamed: R16.2, R17.1
unnamed: C15.1, C16.1, R19.1
unnamed: R19.2, R20.1
unnamed: C25.1, C26.1, R22.1
unnamed: R22.2, R23.1
unnamed: C27.1, C28.1, R25.1
unnamed: R25.2, R26.1
unnamed: C29.1, C30.1, R28.1
unnamed: R28.2, R29.1
unnamed: C31.1, C32.1, R31.1
unnamed: R31.2, R32.1
unnamed: C33.1, C34.1, R34.1
unnamed: R34.2, R35.1
unnamed: C35.1, C36.1, R37.1
unnamed: R37.2, R38.1
unnamed: C37.1, C38.1, R40.1
unnamed: R40.2, R41.1
unnamed: C39.1, C40.1, R43.1
unnamed: R43.2, R44.1
unnamed: C53.1, C54.1, R52.1
unnamed: R52.2, R53.1
unnamed: C55.1, C56.1, R58.1
unnamed: R58.2, R59.1
RLDOUT: R1.2, R5.2, R9.2, R12.2, R15.2, R18.2, R21.2, R24.2, R27.2, R30.2, R33.2, R36.2, R39.2, R42.2, R51.2, R54.2; also elsewhere on the board

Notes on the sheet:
(c) 2022 e-Nable Italia / Alberto Navatta <alberto@e-nableitalia.it> This schematic is licensed with a Creative Common Attribution- NonCommercial-ShareAlike 4.0 International License
8 Channel EMG signal converter Module

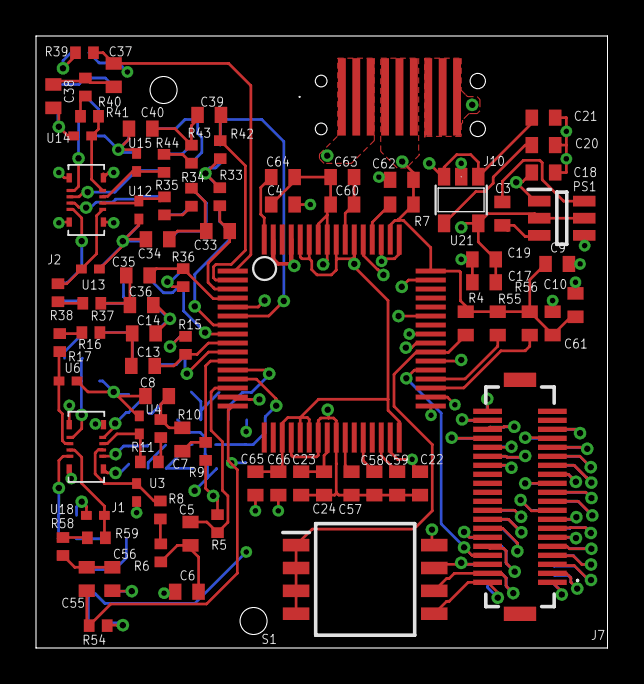
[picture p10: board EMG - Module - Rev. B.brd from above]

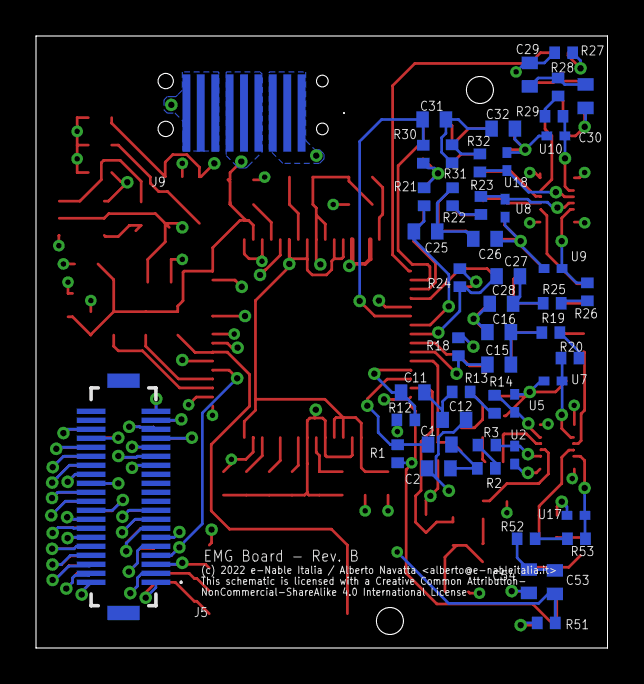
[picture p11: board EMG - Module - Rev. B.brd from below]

Board: 4 copper layers, 31.8 x 34.0 mm, 132 parts (50 on the bottom side), 116 nets.

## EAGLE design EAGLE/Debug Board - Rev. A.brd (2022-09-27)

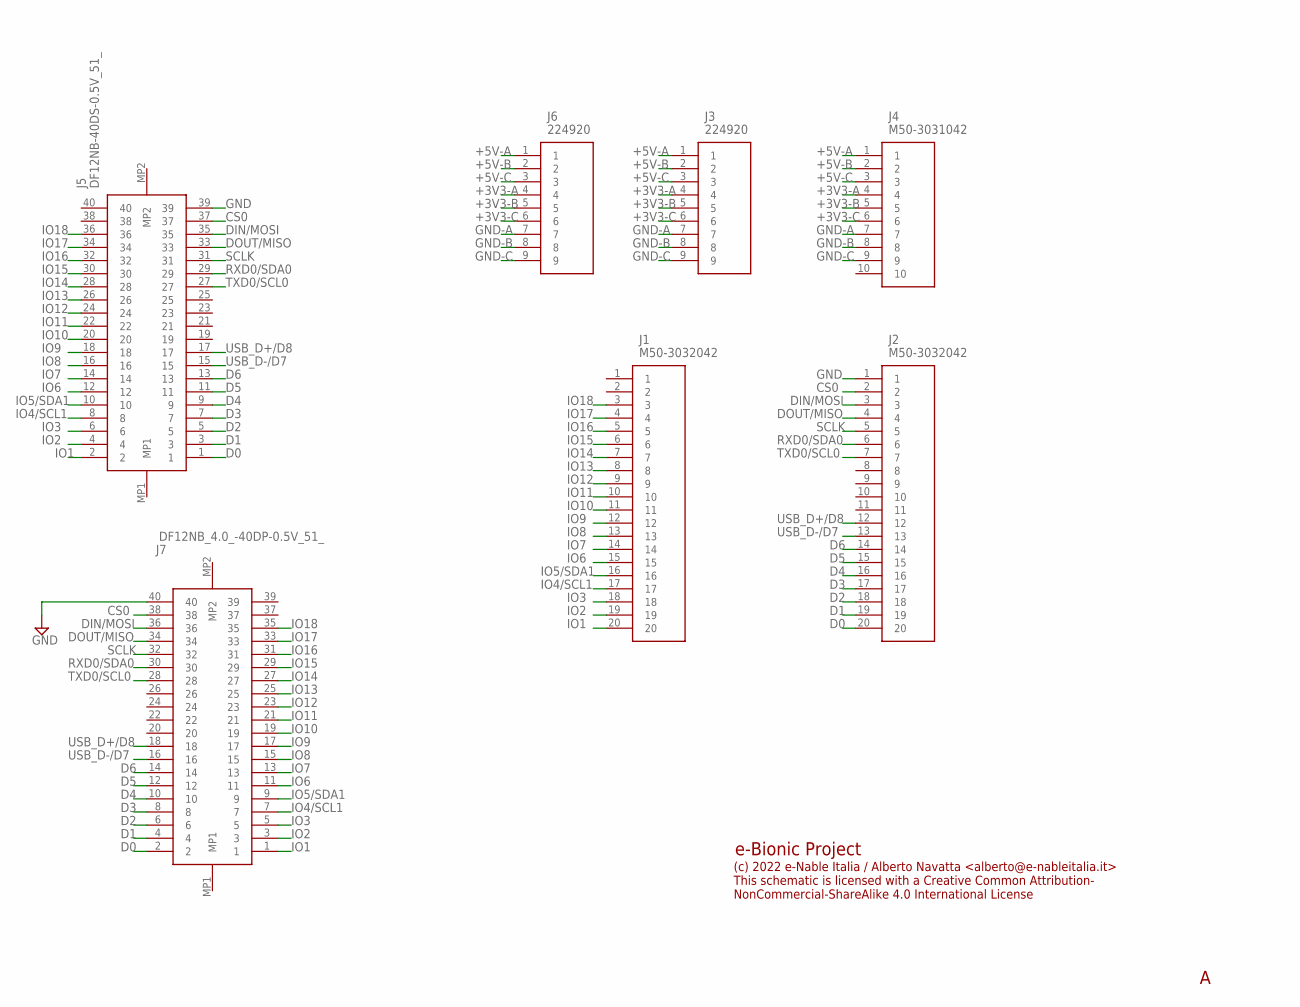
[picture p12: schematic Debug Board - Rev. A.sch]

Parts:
J1, J2: M50-3032042; M503032042
J3, J6: 224920
J4: M50-3031042; M503031042
J5: DF12NB-40DS-0.5V_51_; DF12NB40DS05V51
J7: DF12NB_4.0_-40DP-0.5V_51_; DF12NB4040DP05V51

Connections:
+3V3-A: J3.4, J4.4, J6.4
+3V3-B: J3.5, J4.5, J6.5
+3V3-C: J3.6, J4.6, J6.6
+5V-A: J3.1, J4.1, J6.1
+5V-B: J3.2, J4.2, J6.2
+5V-C: J3.3, J4.3, J6.3
CS0: J2.2, J5.37, J7.38
D0: J2.20, J5.1, J7.2
D1: J2.19, J5.3, J7.4
D2: J2.18, J5.5, J7.6
D3: J2.17, J5.7, J7.8
D4: J2.16, J5.9, J7.10
D5: J2.15, J5.11, J7.12
D6: J2.14, J5.13, J7.14
DIN/MOSI: J2.3, J5.35, J7.36
DOUT/MISO: J2.4, J5.33, J7.34
GND: J2.1, J5.39, J7.40
GND-A: J3.7, J4.7, J6.7
GND-B: J3.8, J4.8, J6.8
GND-C: J3.9, J4.9, J6.9
IO1: J1.20, J5.2, J7.1
IO2: J1.19, J5.4, J7.3
IO3: J1.18, J5.6, J7.5
IO4/SCL1: J1.17, J5.8, J7.7
IO5/SDA1: J1.16, J5.10, J7.9
IO6: J1.15, J5.12, J7.11
IO7: J1.14, J5.14, J7.13
IO8: J1.13, J5.16, J7.15
IO9: J1.12, J5.18, J7.17
IO10: J1.11, J5.20, J7.19
IO11: J1.10, J5.22, J7.21
IO12: J1.9, J5.24, J7.23
IO13: J1.8, J5.26, J7.25
IO14: J1.7, J5.28, J7.27
IO15: J1.6, J5.30, J7.29
IO16: J1.5, J5.32, J7.31
IO17: J1.4, J5.34, J7.33
IO18: J1.3, J5.36, J7.35
RXD0/SDA0: J2.6, J5.29, J7.30
SCLK: J2.5, J5.31, J7.32
TXD0/SCL0: J2.7, J5.27, J7.28
USB_D+/D8: J2.12, J5.17, J7.18
USB_D-/D7: J2.13, J5.15, J7.16

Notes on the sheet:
e-Bionic Project
(c) 2022 e-Nable Italia / Alberto Navatta <alberto@e-nableitalia.it> This schematic is licensed with a Creative Common Attribution- NonCommercial-ShareAlike 4.0 International License

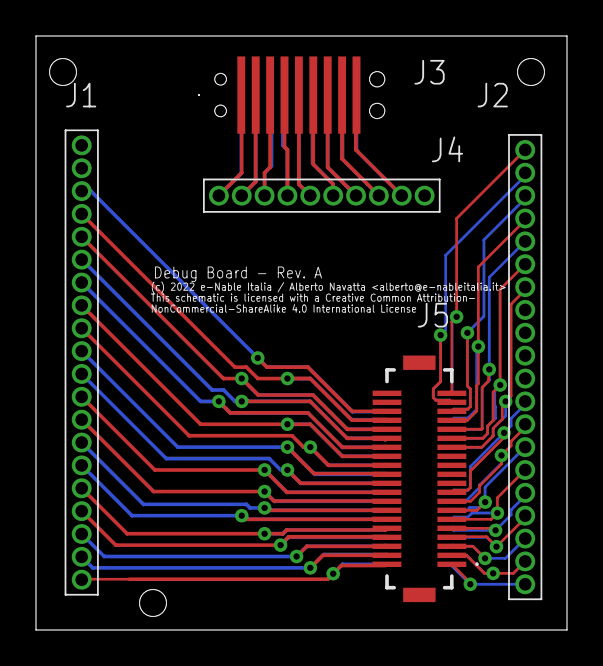
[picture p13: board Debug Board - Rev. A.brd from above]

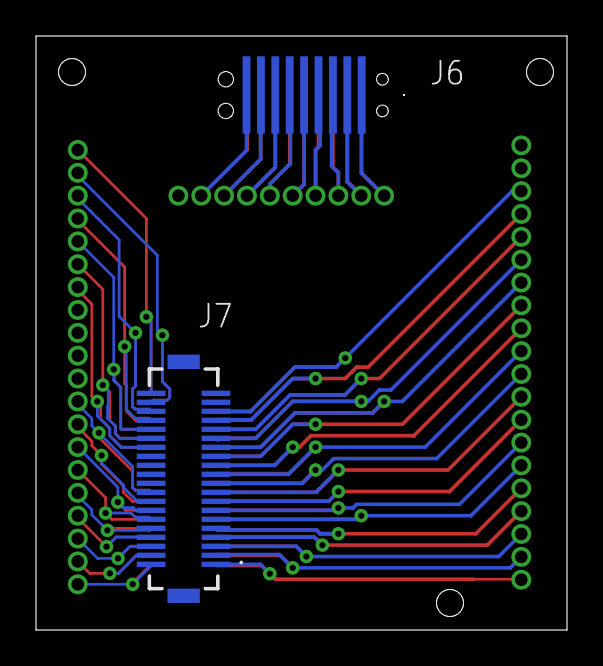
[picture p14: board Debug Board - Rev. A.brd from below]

Board: 2 copper layers, 29.5 x 33.0 mm, 7 parts (2 on the bottom side), 43 nets.

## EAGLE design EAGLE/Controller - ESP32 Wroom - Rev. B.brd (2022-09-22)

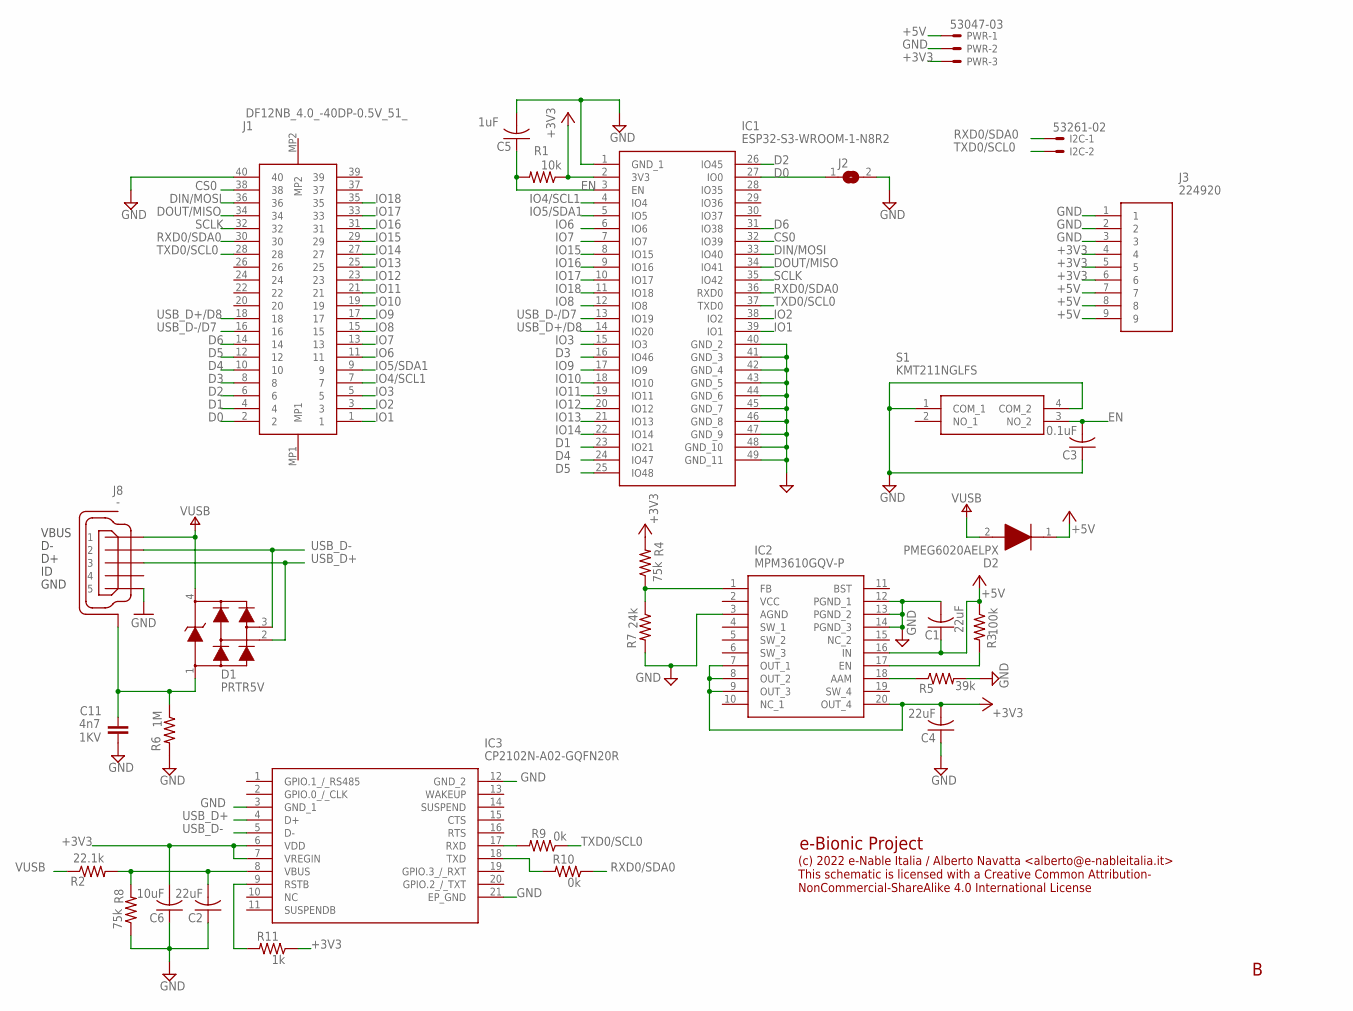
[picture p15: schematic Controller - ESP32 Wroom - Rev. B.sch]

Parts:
C1, C4: 22uF; C0603
C2: 22uF; C0402
C3: 0.1uF; C0402
C5: 1uF; C0402
C6: 10uF; C0402
C11: 4n7; 0805-R2013X50N; VOLTAGE 1KV
D1: PRTR5V; SOT190P230X110-4N
D2: PMEG6020AELPX; SODFL4725X110N
I2C: 53261-02
IC1: ESP32-S3-WROOM-1-N8R2; ESP32S3WROOM1N8R2
IC2: MPM3610GQV-P; MPM3610GQVP
IC3: CP2102N-A02-GQFN20R; CP2102NA02GQFN20
J1: DF12NB_4.0_-40DP-0.5V_51_; DF12NB4040DP05V51
J2: SJ
J3: 224920
J8: -; ZX62-AB-5PA
PWR: 53047-03
R1: 10k; R0402
R2: 22.1k; R0402
R3: 100k; R0402
R4, R8: 75k; R0402
R5: 39k; R0402
R6: 1M; R0402
R7: 24k; R0402
R9, R10: 0k; R0402
R11: 1k; R0402
S1: KMT211NGLFS

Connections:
+3V3: C4.2, C6.2, IC1.2 (3V3), IC2.7 (OUT_1), IC2.8 (OUT_2), IC2.9 (OUT_3), IC2.20 (OUT_4), IC3.6 (VDD), IC3.7 (VREGIN), J3.4, J3.5, J3.6, PWR.3, R1.1, R4.2, R11.1
+5V: C1.1, D2.1 (K), IC2.16 (IN), J3.7, J3.8, J3.9, PWR.1, R3.1
CS0: IC1.32 (IO39), J1.38
D0: IC1.27 (IO0), J1.2, J2.1
D1: IC1.23 (IO21), J1.4
D2: IC1.26 (IO45), J1.6
D3: IC1.16 (IO46), J1.8
D4: IC1.24 (IO47), J1.10
D5: IC1.25 (IO48), J1.12
D6: IC1.31 (IO38), J1.14
DIN/MOSI: IC1.33 (IO40), J1.36
DOUT/MISO: IC1.34 (IO41), J1.34
EN: C3.2, C5.1, IC1.3 (EN), R1.2, S1.3 (NO_2)
GND: C1.2, C2.1, C3.1, C4.1, C5.2, C6.1, C11.2, IC1.1 (GND_1), IC1.40 (GND_2), IC1.41 (GND_3), IC1.42 (GND_4), IC1.43 (GND_5), IC1.44 (GND_6), IC1.45 (GND_7), IC1.46 (GND_8), IC1.47 (GND_9), IC1.48 (GND_10), IC1.49 (GND_11), IC2.3 (AGND), IC2.12 (PGND_1), IC2.13 (PGND_2), IC2.14 (PGND_3), IC3.3 (GND_1), IC3.12 (GND_2), IC3.21 (EP_GND), J1.40, J2.2, J3.1, J3.2, J3.3, J8.5, PWR.2, R5.2, R6.2, R7.2, R8.1, S1.1 (COM_1), S1.4 (COM_2)
IO1: IC1.39 (IO1), J1.1
IO2: IC1.38 (IO2), J1.3
IO3: IC1.15 (IO3), J1.5
IO4/SCL1: IC1.4 (IO4), J1.7
IO5/SDA1: IC1.5 (IO5), J1.9
IO6: IC1.6 (IO6), J1.11
IO7: IC1.7 (IO7), J1.13
IO8: IC1.12 (IO8), J1.15
IO9: IC1.17 (IO9), J1.17
IO10: IC1.18 (IO10), J1.19
IO11: IC1.19 (IO11), J1.21
IO12: IC1.20 (IO12), J1.23
IO13: IC1.21 (IO13), J1.25
IO14: IC1.22 (IO14), J1.27
IO15: IC1.8 (IO15), J1.29
IO16: IC1.9 (IO16), J1.31
IO17: IC1.10 (IO17), J1.33
IO18: IC1.11 (IO18), J1.35
unnamed: IC2.18 (AAM), R5.1
unnamed: C2.2, IC3.8 (VBUS), R2.2, R8.2
unnamed: IC2.1 (FB), R4.1, R7.1
unnamed: IC2.17 (EN), R3.2
unnamed: IC3.17 (RXD), R9.2
unnamed: IC3.18 (TXD), R10.2
unnamed: C11.1, D1.1, J8.6 (SH), J8.7 (SH), J8.8 (SH), J8.9 (SH), J8.10 (SH), J8.11 (SH), R6.1
unnamed: IC3.9 (RSTB), R11.2
RXD0/SDA0: I2C.1, IC1.36 (RXD0), J1.30, R10.1
SCLK: IC1.35 (IO42), J1.32
TXD0/SCL0: I2C.2, IC1.37 (TXD0), J1.28, R9.1
USB_D+: D1.2, IC3.4 (D+), J8.3
USB_D+/D8: IC1.14 (IO20), J1.18
USB_D-: D1.3, IC3.5 (D-), J8.2
USB_D-/D7: IC1.13 (IO19), J1.16
VUSB: D1.4, D2.2 (A), J8.1, R2.1

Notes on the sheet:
e-Bionic Project
(c) 2022 e-Nable Italia / Alberto Navatta <alberto@e-nableitalia.it> This schematic is licensed with a Creative Common Attribution- NonCommercial-ShareAlike 4.0 International License

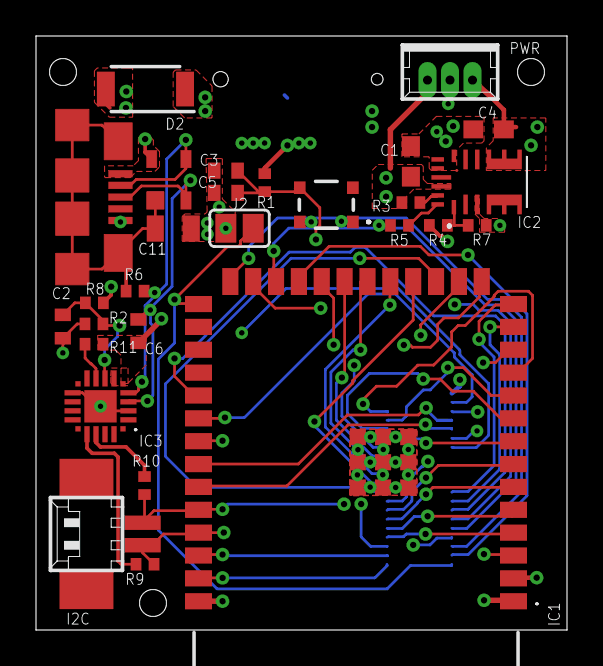
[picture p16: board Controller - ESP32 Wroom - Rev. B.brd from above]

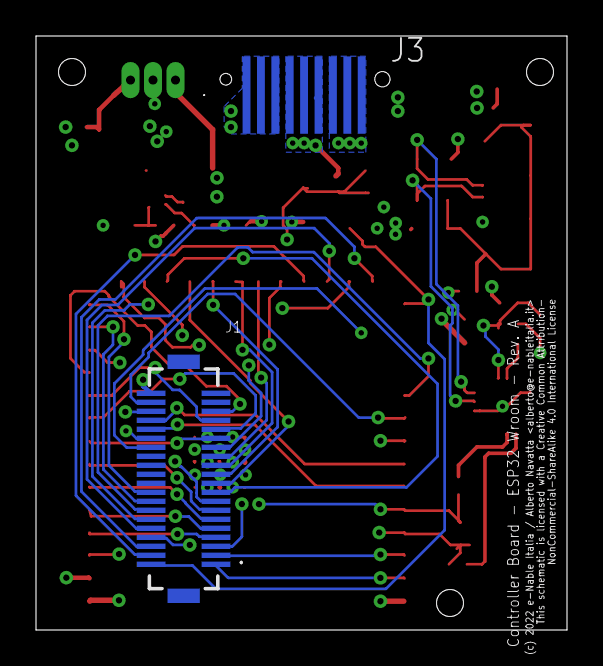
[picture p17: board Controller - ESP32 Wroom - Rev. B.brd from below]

Board: 4 copper layers, 29.5 x 33.0 mm, 30 parts (2 on the bottom side), 48 nets.

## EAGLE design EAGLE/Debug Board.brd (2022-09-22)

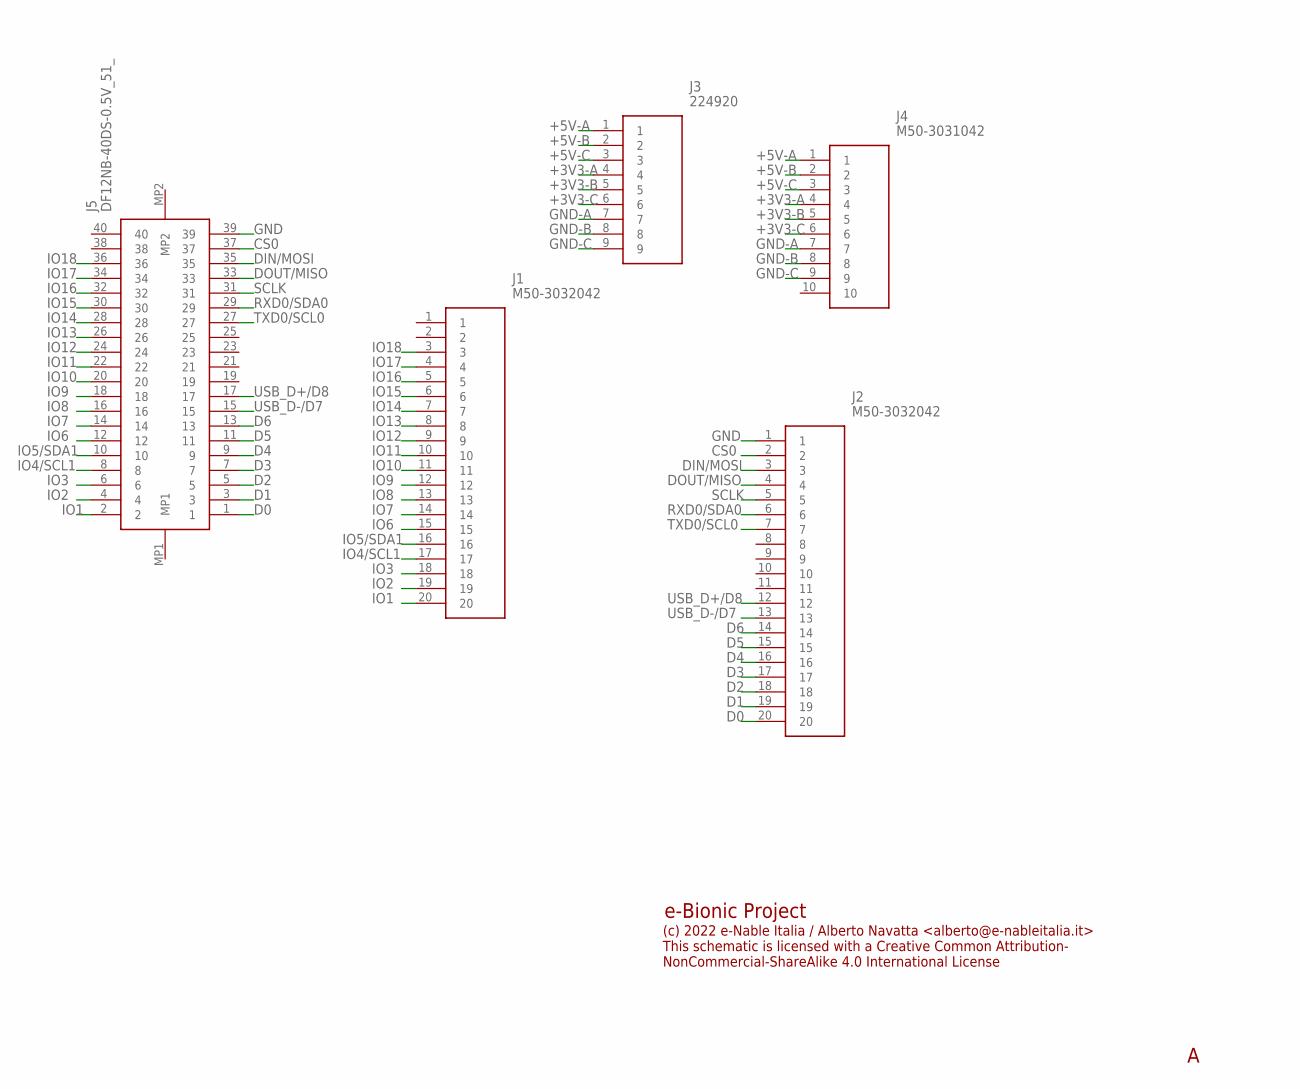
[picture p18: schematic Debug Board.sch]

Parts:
J1, J2: M50-3032042; M503032042
J3: 224920
J4: M50-3031042; M503031042
J5: DF12NB-40DS-0.5V_51_; DF12NB40DS05V51

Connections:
+3V3-A: J3.4, J4.4
+3V3-B: J3.5, J4.5
+3V3-C: J3.6, J4.6
+5V-A: J3.1, J4.1
+5V-B: J3.2, J4.2
+5V-C: J3.3, J4.3
CS0: J2.2, J5.37
D0: J2.20, J5.1
D1: J2.19, J5.3
D2: J2.18, J5.5
D3: J2.17, J5.7
D4: J2.16, J5.9
D5: J2.15, J5.11
D6: J2.14, J5.13
DIN/MOSI: J2.3, J5.35
DOUT/MISO: J2.4, J5.33
GND: J2.1, J5.39
GND-A: J3.7, J4.7
GND-B: J3.8, J4.8
GND-C: J3.9, J4.9
IO1: J1.20, J5.2
IO2: J1.19, J5.4
IO3: J1.18, J5.6
IO4/SCL1: J1.17, J5.8
IO5/SDA1: J1.16, J5.10
IO6: J1.15, J5.12
IO7: J1.14, J5.14
IO8: J1.13, J5.16
IO9: J1.12, J5.18
IO10: J1.11, J5.20
IO11: J1.10, J5.22
IO12: J1.9, J5.24
IO13: J1.8, J5.26
IO14: J1.7, J5.28
IO15: J1.6, J5.30
IO16: J1.5, J5.32
IO17: J1.4, J5.34
IO18: J1.3, J5.36
RXD0/SDA0: J2.6, J5.29
SCLK: J2.5, J5.31
TXD0/SCL0: J2.7, J5.27
USB_D+/D8: J2.12, J5.17
USB_D-/D7: J2.13, J5.15

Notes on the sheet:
e-Bionic Project
(c) 2022 e-Nable Italia / Alberto Navatta <alberto@e-nableitalia.it> This schematic is licensed with a Creative Common Attribution- NonCommercial-ShareAlike 4.0 International License

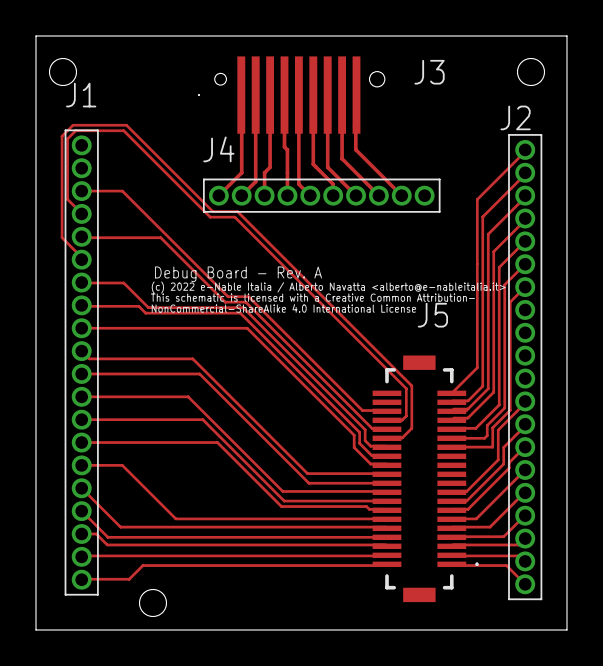
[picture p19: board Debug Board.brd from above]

Board: 2 copper layers, 29.5 x 33.0 mm, 5 parts (0 on the bottom side), 43 nets.

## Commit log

2022-09-13 Added latest release of ESP32 Controller board
    [Controller - ESP32 Wroom - Rev. 0.9.brd, Controller - ESP32 Wroom - Rev. 0.9.sch]
2022-09-13 directory layout review
    [Controller - ESP32 Wroom - Rev. 0.9.brd, Controller - ESP32 Wroom - Rev. 0.9.sch]
2022-09-18 [BION-1] completed review of controller board, changes
    1) Wrong side for power connector
    2) Removed signals from ground plane
    3) JTAG connector is optional, changed with a smal one to reduce footprint
    [Controller - ESP32 Wroom - Rev. A.brd, Controller - ESP32 Wroom - Rev. A.sch]
2022-09-18 [BION-1] Added board and schematics PDF
2022-09-19 [BION-1] Removed old version files
    * removed Rev. 0.9 files
    * removed jtag connector, JTAG PINs can be extracted from J1 connector
    [Controller - ESP32 Wroom - Rev. 0.9.brd, Controller - ESP32 Wroom - Rev. 0.9.sch]
2022-09-19 Added board revision & copyrights on PCB
    [Controller - ESP32 Wroom - Rev. A.brd]
2022-09-19 Fixed some clearance error
    [Controller - ESP32 Wroom - Rev. A.brd]
2022-09-19 Changed some via to be passthrought
    Added schematic and new board layout prints
    [Controller - ESP32 Wroom - Rev. A.brd]
2022-09-22 Added: * Rev. B Controller Board * Debug Board
    [Controller - ESP32 Wroom - Rev. B.brd, Controller - ESP32 Wroom - Rev. B.sch, Debug Board.brd, Debug Board.sch]
2022-09-22 Added Rev. B Controller Board & Rev. A Debug Board
    [Controller - ESP32 Wroom - Rev. B.brd, Controller - ESP32 Wroom - Rev. B.sch, Debug Board.brd, Debug Board.sch]
2022-09-27 Updated Debug Board to Rev. A:
    Added power and data bus connector on the bottom side of the board
    [Debug Board - Rev. A.brd, Debug Board - Rev. A.sch]
2022-10-16 Added BOMs, fixed some typo in presentation
    [BOM_Prod_Controller_Board_W309348AS1Y7_Prod_T-1Y8W309348A.xlsx, BOM_Prod_Debug_Board_W309348AS1Y5_Prod_T-1Y6W309348A.xlsx]
2023-03-05 Added EMG EMG - Module - Rev. B board, updated BOMs and build directory
    [BOM_Prod_EMG_Board.xlsx, BOM_Prod_EMG_Jack_Connector.xlsx, EMG - Module - Rev. B.brd, EMG - Module - Rev. B.sch]

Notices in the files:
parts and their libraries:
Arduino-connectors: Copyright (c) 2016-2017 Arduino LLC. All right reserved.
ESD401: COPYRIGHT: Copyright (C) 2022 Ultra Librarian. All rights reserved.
